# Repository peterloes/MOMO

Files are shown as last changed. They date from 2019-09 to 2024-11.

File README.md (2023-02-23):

# Multifunctional mainboard to observe and manipulate organisms (MOMO)
[\[paper\]](https://besjournals.onlinelibrary.wiley.com/doi/full/10.1111/1365-2656.13160) 2.3 Nest and feeder monitoring system

Authors: Loës P., Skripsky P., Kempenaers B. (2019) 

Platform for animal observation and manipulation. 

An efficient system to monitor and control animal behaviour in wildlife
as well as in laboratory settings.

- Targeted manipulation of 1000 and more individuals. Selective feeder.
- Supports a broad range of technical applications like e.g. traps, gates, feeders, lights, cameras
-	Compatible with different RFID systems and triggers
-	Low power consumption and specific data collection lead to long lasting collection periods
-	Applicable world-wide due to its compatibility with different types of radio clock receivers 
-	High observation quality through low disturbance to the animals
- Supports data-transfer to external devices, such as personal computers

My image

- Time Synchronization with atomic clock once a day to ensure optimal data quality
- Application Current Control twice a day
- Forecast for Battery-Change implemented
- Energy Bypass so that Date and Time are maintained even when changing battery
- Hyperterminal Output to get real-time data to the computer/laptop
- Low-Power Device:sleep: 220µA@12V with Light_Barrier awake: 12mA@12V

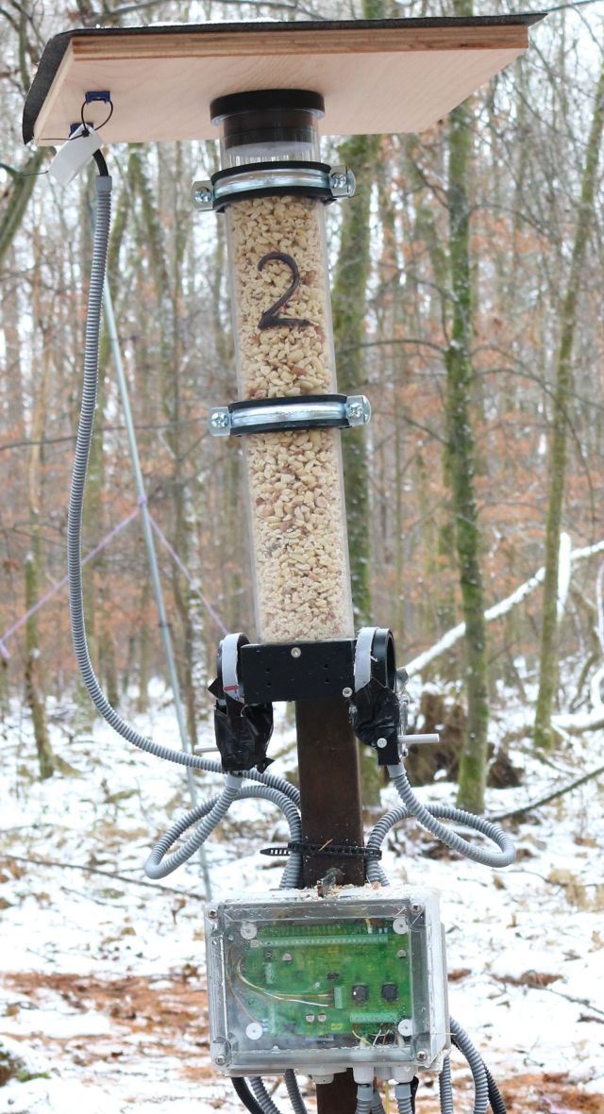
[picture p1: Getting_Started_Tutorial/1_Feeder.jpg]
My image


Bird Feeder Application:

https://github.com/peterloes/MOMO/blob/master/Getting_Started_Tutorial/1_poster_overview_3.pdf

Raw data on SD Card:

https://github.com/peterloes/MOMO/blob/master/Getting_Started_Tutorial/6_rawdata_BOX1005.TXT

Configuration data on SD Card:

https://github.com/peterloes/MOMO/blob/master/Software/CONFIG.TXT

Optional components: 

https://github.com/peterloes/Light_Barrier

https://github.com/peterloes/Servo_Engine

https://github.com/peterloes/Linear_Engine

https://github.com/peterloes/Booter_RFID-MS_MOMO_TAMDL

https://github.com/peterloes/Clock_receiver_RFID-MS_MOMO_TAMDL

Manufacture:

https://github.com/peterloes/MOMO/blob/master/Getting_Started_Tutorial/5_Supplier.txt

EXTENSIONS

Application Scales: Outdoor weighing system for animals include RFID-reader

https://github.com/peterloes/Scales

Application Audio: Record and playback soundfiles triggered by (RFID) pit-tag numbers

https://github.com/peterloes/Audio

C is the Greenest Programming Language

To achieve its power and energy-efficiency features, EFM32 products utilize ultralow active and idle power,
fast wakeup and processing times, and most important, the ability to intelligently interact with peripherals
and sensors autonomously without waking up the CPU and consuming more power.

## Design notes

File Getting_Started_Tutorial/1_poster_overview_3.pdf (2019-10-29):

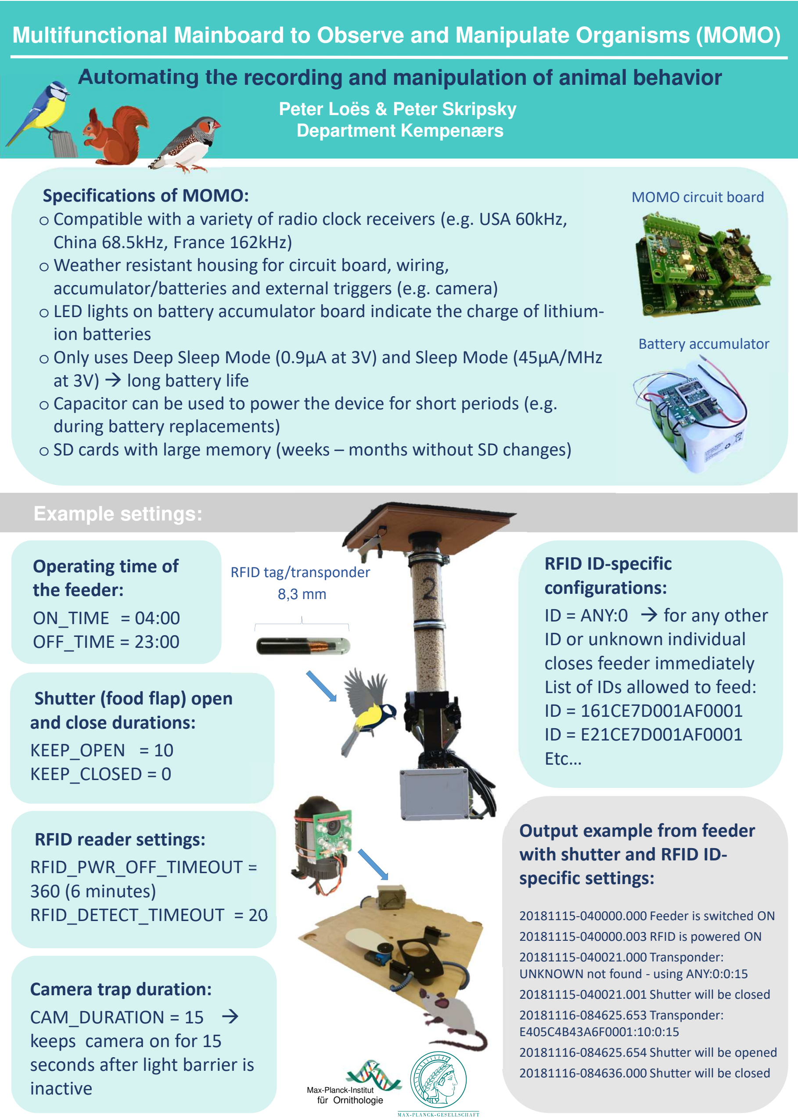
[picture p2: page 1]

### Multifunctional Mainboard to Observe and Manipulate Organisms (MOMO)

### Automating the recording and manipulation of animal behavior

Peter Loës & Peter Skripsky Department Kempenærs

Operating time of
the feeder:
ON_TIME = 04:00
OFF_TIME = 23:00

8,3 mm

RFID tag/transponder

RFID reader settings:
RFID_PWR_OFF_TIMEOUT =
360 (6 minutes)
RFID_DETECT_TIMEOUT = 20

Shutter (food flap) open
and close durations:
KEEP_OPEN = 10
KEEP_CLOSED = 0

Camera trap duration:
CAM_DURATION = 15 →
keeps camera on for 15
seconds after light barrier is inactive

RFID ID-specific
configurations:
ID = ANY:0 → for any other ID or unknown individual
closes feeder immediately
List of IDs allowed to feed: ID = 161CE7D001AF0001
ID = E21CE7D001AF0001
Etc…
Specifications of MOMO: | MOMO circuit board
- Compatible with a variety of radio clock receivers (e.g. USA 60kHz,
China 68.5kHz, France 162kHz)
- Weather resistant housing for circuit board, wiring,
accumulator/batteries and external triggers (e.g. camera)
- LED lights on battery accumulator board indicate the charge of lithiumion batteries
- Only uses Deep Sleep Mode (0.9μA at 3V) and Sleep Mode (45μA/MHz at 3V) → long battery life
- Capacitor can be used to power the device for short periods (e.g. during battery replacements)
- SD cards with large memory (weeks – months without SD changes)

Max-Planck-Institut
für Ornithologie

Example settings:

Battery accumulator

Output example from feeder with shutter and RFID ID-specific settings:

20181115-040000.000 Feeder is switched ON 20181115-040000.003 RFID is powered ON 20181115-040021.000 Transponder: UNKNOWN not found - using ANY:0:0:15 20181115-040021.001 Shutter will be closed 20181116-084625.653 Transponder: E405C4B43A6F0001:10:0:15
20181116-084625.654 Shutter will be opened 20181116-084636.000 Shutter will be closed

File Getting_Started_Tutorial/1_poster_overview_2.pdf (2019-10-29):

### Multifunctional Mainboard to Observe and Manipulate Organisms (MOMO)

### Automating the recording and manipulation of animal behavior

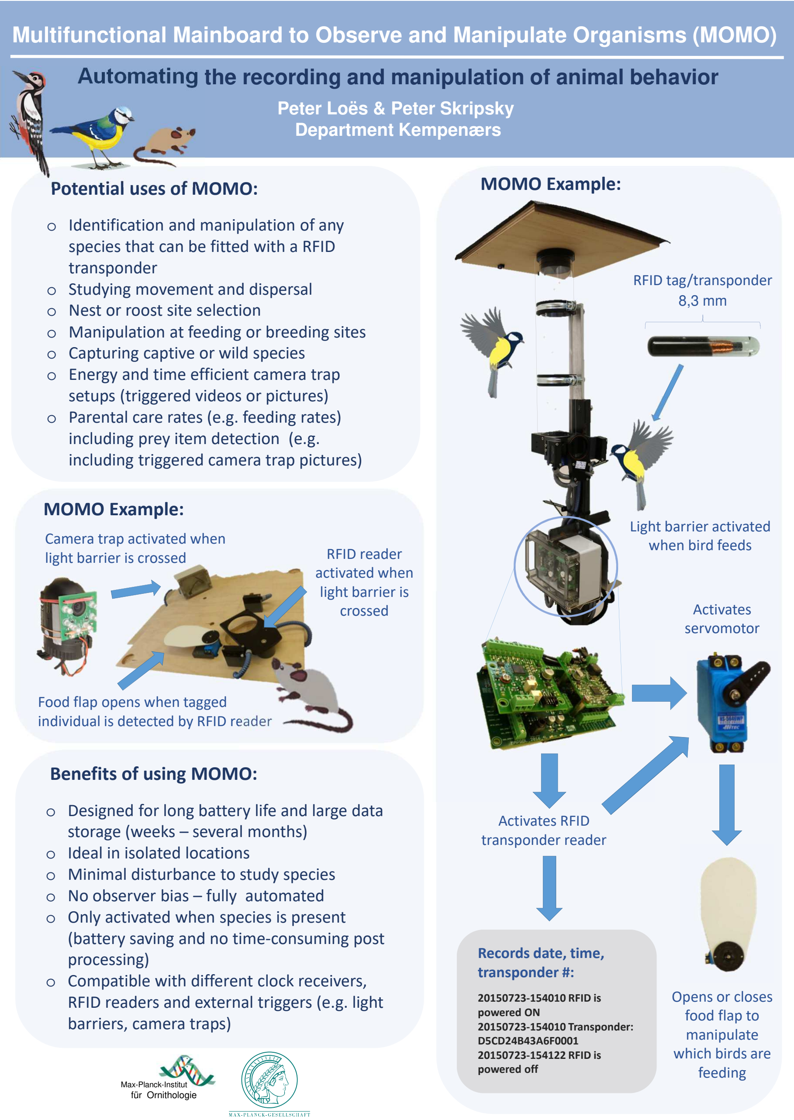
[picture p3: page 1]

Peter Loës & Peter Skripsky Department Kempenærs

Max-Planck-Institut
für Ornithologie

8,3 mm

RFID tag/transponder

Activates
servomotor

Opens or closes
food flap to
manipulate
which birds are
feeding

Light barrier activated
when bird feeds

Activates RFID
transponder reader

Records date, time,
transponder #:

20150723-154010 RFID is
powered ON
20150723-154010 Transponder: D5CD24B43A6F0001
20150723-154122 RFID is
powered off
Potential uses of MOMO: | MOMO Example:
- Identification and manipulation of any
species that can be fitted with a RFID
transponder
- Studying movement and dispersal
- Nest or roost site selection
- Manipulation at feeding or breeding sites
- Capturing captive or wild species
- Energy and time efficient camera trap setups (triggered videos or pictures)
- Parental care rates (e.g. feeding rates) including prey item detection (e.g. including triggered camera trap pictures)

Food flap opens when tagged individual is detected by RFID reader

RFID reader
activated when
light barrier is
crossed

Camera trap activated when light barrier is crossed

Benefits of using MOMO:

- Designed for long battery life and large data storage (weeks – several months)
- Ideal in isolated locations
- Minimal disturbance to study species
- No observer bias – fully automated
- Only activated when species is present (battery saving and no time-consuming post processing)
- Compatible with different clock receivers, RFID readers and external triggers (e.g. light barriers, camera traps)

MOMO Example:

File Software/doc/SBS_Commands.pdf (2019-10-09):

# Projekt U-BMS2-4

# SBS-

# Commands

# SBS Commands

Device Address | | | | | | 0x0A
ManufacturerAccess | | | | | | 0x00

Read word

RemainingCapacityAlarm | 0x01

Read word
Rückgabe des remainingCapacityAlarm-Wertes in [mAh].

Wenn die Restkapazität(remainingCapacity) kleiner als der Wert vom RemainingCapacityAlarm ist, sendet die Batterie eine Alarmwarnung zum Host. Der RemainingCapacityAlarm-Flag im Battery-Status wird gesetzt.

RemainingTimeAlarm | 0x02

Read word
Rückgabe des remainingTimeAlarm -Wertes in [min].

Wenn die durchschnittliche Entladezeit des Akkus(AverageTimeToEmpty) kleiner als der Wert vom
RemainingTimeAlarm | ist, | sendet | die | Batterie | eine | Alarmwarnung | zum | Host. | Der
RemainingTimeAlarm-Flag im Battery-Status wird gesetzt.
Battery Mode | | | | | | 0x03

Read word

Bit | Beschreibung

### 12 BALANCING CELL3

### 11 BALANCING CELL2

### 10 BALANCING CELL1

### 6 BALANCING CELL4

### 5 Deep Under Voltage recovery(DUVRD) Bit vom FET Control and Status-Register

(FCSR)

### 4 Current Protection Status (CPS) Bit vom FET Control and Status-Register (FCSR)

### 3 Discharge FET (DFE) Bit vom FET Control and Status-Register (FCSR)

### 2 Charge FET (CFE) Bit vom FET Control and Status-Register (FCSR)

CoreTemperature | 0x08

Read word
Die aktuelle Chip-Temperatur in [°K]
Voltage | 0x09

Read word
Die gesamte Akkuspannung in [mV]
BatteryCurrent | 0x0A

Read word
Der aktuelle Strom in [mA], der aus bzw. in den Akkupack durchfließt.
BatteryAverageCurrent | 0x0B

Read word
Der durchschnittliche Strom des Akkupacks in [mA]
RelativeStateOfCharge | 0x0D

Read word
Der relative Ladezustand des Akkupacks in [%]
AbsoluteStateOfCharge | 0x0E

Read word
Der absolute Ladezustand des Akkupacks in [%]
RemainingCapacity | 0x0F

Read word
Die Restkapazität des Akkupacks in [mAh]
FullChargeCapacity | 0x10

Read word
Rückgabe der vollen Ladekapazität in [mAh]
RunTimeToEmpty | 0x11

Read word
Die Ladezeit in [min]
AverageTimeToEmpty | 0x12

Read word
Die durchschnittliche Entladezeit [min]
AverageTimeToFull | 0x13

Read word
Die durchschnittliche Ladezeit in [min]

ChargingCurrent | 0x14

Read word
Der Ladestrom in [mA]
ChargingVoltage | 0x15

Read word
Die maximale Ladespannung in [mV]
Battery Status (flags) | 0x16

Read word

Bit | Beschreibung

### 15 Over Charged Alarm

Überprüfung des chargingProhibited-Flags

### 14 Terminate Charge Alarm

Überprüfung des voltageTooHigh-Flags

### 12 Over Temp Alarm

Überprüfung des cellTemperatureTooHigh -Flags

### 11 Terminante Discharge Alarm

Dieses Bit wird gesetzt, wenn die Restkapazität unter dem definierten Wert von SBS_TERMINATE_DISCHARGE_LIMIT (Standard 5mAh) liegt. Wenn ein Ladegerät erkannt wird, wird dieses Bit gelöscht.

### 10 Battery Protection Triggered

Dieses Bit wird gesetzt, wenn die Batterieschutz-Hardware die FETs ausschaltet.

### 9 Remaining Capacity Alarm

Dieses Bit wird gesetzt, wenn die Restkapazität weniger als der definierte Wert des Restkapazität-Alarms(RemainingCapacityAlarm) ist.

### 8 Remaining Time Alarm :

Wenn die durchschnittlische Entladezeit (AverageTimeToEmpty) kleiner als der definierte Wert des Entladezeit-Alarms (RemainingTimeAlarm) ist, wird dieses Bit gesetzt.

### 7 Initialized

Dieses Bit wird gesetzt, wenn die Initialisierung erfolgreich abgeschlossen ist.

### 6 Discharging

Dieses Bit wird gesetzt, wenn ein Entladestrom fließt.

### 5 Fully Charged

Dieses Bit wird gesetzt, wenn die Batterie vollständig geladen ist. Wenn ein Entladestrom aus der Batterie fließt, der höher als der Standby-Stromwert ist, wird dieses Bit gelöscht.

### 4 Fully Discharged

Dieses Bit wird gesetzt, wenn die Restkapazität der Batterie bzw. die Zellenspannung sehr niedrig ist. Wenn der relative Ladezustand über 20% steigt, wird dieses Bit gelöscht.

ChargerCycleCount | 0x17

Read word
Die Anzahl der Ladezyklen
DesignCapacity | 0x18

Read word
Die Nennkapazität in [mAh]
DesignVoltage | 0x19

Read word
Die Nennspannung in [mV]
SpecificationInfo | 0x1A

Read word
Die Spezifikation-Info (Version und Revision-Nummer)
ManufactureDate | 0x1B

Read word
Das Herstellungsdatum
SerialNumber | 0x1C

Read word
Die Seriennummer
ManufacturerName | 0x20

Read Block
Der Name des Herstellers
DeviceName | 0x21

Read Block
Der Name des Gerätes
DeviceChemistry | 0x22

Read Block
Die chemische Bezeichnung des Gerätes
ManufacturerData | 0x23

Read Block
Die Herstellerdaten
ShuntResistance | 0x2A

Read word
Der Wert des Shunt-Widerstands in [µOhm]

CellsInSeries | 0x3C

Read word
Anzahl der verwendeten Zellen in Serie
OverCurrentReactionTime | 0x3D

Read word
Überstrom Reaktionszeit Stufe 1
OverCurrentCharge | 0x3E

Read word
Überladestrom Stufe 1
OverCurrentDischarge | 0x3F

Read word
Überentladestrom Stufe 1
HighCurrentReactionTime | 0x40

Read word
Überstrom Reaktionszeit Stufe 2
HighCurrentCharge | 0x41

Read word
Überladestrom Reaktionszeit Stufe 2
HighCurrentDischarge | 0x42

Read word
Überentladestrom Stufe 2
VoltageCell4 | 0x44

Read word
Rückgabe der Spannung der Zelle 4 in [mV]
VoltageCell3 | 0x45

Read word
Rückgabe der Spannung der Zelle 3 in [mV]
VoltageCell2 | 0x46

Read word
Rückgabe der Spannung der Zelle 3 in [mV]

VoltageCell1 | 0x47

Read word
Rückgabe der Spannung der Zelle 1 in [mV]
CellMinVoltage | 0x54

Read word
Die minimale Zellenspannung in [mV]
CellMaxVoltage | 0x55

Read word
Der Wert der maximalen Zellenspannung in [mV]
CellPowerOffVoltage | 0x55

Read word
Der Wert der Zellenspannung in [mV], bei der das BMS in den PowerOffModus geht

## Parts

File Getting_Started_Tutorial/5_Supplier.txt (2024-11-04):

Active antennas
DCF77 Empfänger AASV DCFn PON/Ri/1m Aktivantenne SV DCFn 

HKW-Elektronik GmbH
Jörg Schneider

Eisenacher Str. 42 b
99848 Wutha-Farnroda / Thür.
Germany
Phone:  +49 (0)36921 3080 130
mailto:    schneider@hkw-elektronik.de
www.hkw-elektronik.de

Lightbarriers for front plate
Doppel - Lichtschranke Art.Nr. P00700 (Lichtschranken in Frontplatten):

SWISSSENSOR AG
Geschäftsleitung Hermann Beer

Steinacherstrasse 4
CH-9327 Tübach
Germany
Tel. +41(0)71 845 24 24
mailto:beer@swisssensor.ch
www.swisssensor.ch

Lithium Ionen rechargeable battery pack Art.Nr. 60.16294 Panasonic NCR 18650GA 4S2P
14,4Volt 6900mAh inklusive SMBus Kabel je. 150mm 

DYNAMIS Batterien GmbH
Josef Pfeil

Brühlstraße 15  D- 78465 Dettingen / Konstanz
Tel. +49 (0) 75 33/93 669-15
mailto:josef.pfeil@dynamis-batterien.de
www.dynamis-batterien.de

RFID reader
Nanomodule Multi 125LV A/1.11 (T3NM-LV) 125kHz +/-0,5% Art.Nr. ART10413
ANT002 Rundspule 47mm, 490µH Art.Nr. ART 10668

Elatec GmbH
Felix Ellspermann

Zeppelinstr. 1
82178 Puchheim 
Germany
Tel: +49 89 552 9961 120
mailto: f.ellspermann@elatec.com
www.elatec-rfid.com

Small sized transponder, not uniqued.
GlassTag 1,41x8,3mm EM4305 134kHz

Programming required for transponders.

Rasmus Forntheil
Product Manager Animal ID
RBIS Europe, Smartrac Specialty GmbH

e: rasmus.forntheil@eu.averydennison.com
t: +49 (0) 2265 9919-14  |  m: +49 (0) 173 5688184
Gewerbeparkstr. 10, 51580 Reichshof-Wehnrath, Germany

Internet: https://www.averydennison.com/en/home.html

Supplier of all Electronic Boards

Top-Print Electronic GmbH
Oskar Schmid

Rosenheimer Landstr. 129a
85521 Ottobrunn
Germany
Tel.: +49-89-60668047
Fax: +49-89-60668049
mailto: info@top-print.eu
https://www.leiterplatten-muenchen.de/

Protective coating with Schmelzharz Bectron MR3404

KC – Kunststoff- Chemische Produkte GmbH
Holger Sarau-Burghardt

Leonberger Straße 86 
DE 71292 Friolzheim
phone: +49 (0)7044 9425 13
e-mail: h.sarau-burghardt@kc-produkte.com
http: www.conformalcoating.de

Industrial SD Cards ATP 2GB
https://www.atpinc.com/products/industrial-sd-cards

FTDI Chip cable (3.5mm Audio Jack to USB)
TTL-232R-3V3-AJ

Housing
https://www.spelsberg.de/industrieleergehaeuse/glatt-mit-befestigungsnocken/20100701/
TG PC 1612-9-to
Artikelnummer: 20100701 | Maße: 162 x 122 x 90 mm
Leergehäuse IP66 / IP67 Polycarbonat

Docklight RS232 Terminal / RS232 Monitor
https://docklight.de/information/

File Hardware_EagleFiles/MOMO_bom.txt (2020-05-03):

Partlist exported at 5/22/2017 10:02:44 AM

Part  Value                 Device                  Package                Description                                                    MF MPN     OC_FARNELL OC_NEWARK PACKAGE  SUPPLIER         
C1    100µF/25V             CPOL-EUE                PANASONIC_E            POLARIZED CAPACITOR, European symbol                                                                                     
C2    10µF/25V              C-EUC1206               C1206                  CAPACITOR, European symbol                                                                                               
C3    22µF/10V              C-EUC0603               C0603                  CAPACITOR, European symbol                                                                                               
C4    EECS0HD 224;Panasonic GOLDCAPSPK-V            GOLDCAPSPK-V                                                                                                                                    
C5    100µF/25V             CPOL-EUE                PANASONIC_E            POLARIZED CAPACITOR, European symbol                                                                                     
C6    100µF/25V             CPOL-EUE                PANASONIC_E            POLARIZED CAPACITOR, European symbol                                                                                     
C7    100µF/25V             CPOL-EUE                PANASONIC_E            POLARIZED CAPACITOR, European symbol                                                                                     
C8    100nF/16V             C-EUC0805               C0805                  CAPACITOR, European symbol                                                                                               
C9    100nF/16V             C-EUC0805               C0805                  CAPACITOR, European symbol                                                                                               
C10   100nF/16V             C-EUC0805               C0805                  CAPACITOR, European symbol                                                                                               
C11   10µ/25V               C-EUC1206               C1206                  CAPACITOR, European symbol                                                                                               
C12   100n                  C_SMD0805               0805                                                                                                                                            
C13   1u                    C_SMD0805               0805                                                                                                                                            
C14   12p                   C_SMD0805               0805                                                                                                                                            
C15   18p                   C_SMD0805               0805                                                                                                                                            
C16   100n                  C_SMD0805               0805                                                                                                                                            
C17   100n                  C_SMD0805               0805                                                                                                                                            
C18   100n                  C_SMD0805               0805                                                                                                                                            
C19   12p                   C_SMD0805               0805                                                                                                                                            
C20   18p                   C_SMD0805               0805                                                                                                                                            
C21   10µ                   C_SMD0805               0805                                                                                                                                            
C22   100n                  C_SMD0805               0805                                                                                                                                            
C23   100n                  C_SMD0805               0805                                                                                                                                            
C24   100n                  C_SMD0805               0805                                                                                                                                            
C25   100n                  C_SMD0805               0805                                                                                                                                            
C26   100n                  C_SMD0805               0805                                                                                                                                            
C27   10µ                   C_SMD0805               0805                                                                                                                                            
C28   100nF                 C-EUC0603               C0603                  CAPACITOR, European symbol                                                                                               
C29   100nF                 C-EUC0603               C0603                  CAPACITOR, European symbol                                                                                               
C30   100nF                 C-EUC0603               C0603                  CAPACITOR, European symbol                                                                                               
C31   100nF                 C-EUC0603               C0603                  CAPACITOR, European symbol                                                                                               
C32   100nF                 C-EUC0603               C0603                  CAPACITOR, European symbol                                                                                               
C33   4.7µF                 C-EUC1210               C1210                  CAPACITOR, European symbol                                                                                               
C34   4.7µF                 C-EUC1210               C1210                  CAPACITOR, European symbol                                                                                               
C35   n.b.                  C-EUC1210               C1210                  CAPACITOR, European symbol                                                                                               
C36   n.b.                  C-EUC1210               C1210                  CAPACITOR, European symbol                                                                                               
C37   10nF                  C-EUC0603               C0603                  CAPACITOR, European symbol                                                                                               
C38   10nF                  C-EUC0603               C0603                  CAPACITOR, European symbol                                                                                               
C39   100nF                 C-EUC0603               C0603                  CAPACITOR, European symbol                                                                                               
C40   100nF                 C-EUC0603               C0603                  CAPACITOR, European symbol                                                                                               
C41    n.b.                 C-EUC0603               C0603                  CAPACITOR, European symbol                                                                                               
C42    n.b.                 C-EUC0603               C0603                  CAPACITOR, European symbol                                                                                               
C43   4.3nF                 C-EUC0603               C0603                  CAPACITOR, European symbol                                                                                               
C44   4.3nF                 C-EUC0603               C0603                  CAPACITOR, European symbol                                                                                               
C45   24pF                  C-EUC0603               C0603                  CAPACITOR, European symbol                                                                                               
C46   24pF                  C-EUC0603               C0603                  CAPACITOR, European symbol                                                                                               
C47    n.b.                 C-EUC0603               C0603                  CAPACITOR, European symbol                                                                                               
C48    n.b                  C-EUC0603               C0603                  CAPACITOR, European symbol                                                                                               
C49   22µF                  C-EUC1210               C1210                  CAPACITOR, European symbol                                                                                               
C50   22µF                  C-EUC1210               C1210                  CAPACITOR, European symbol                                                                                               
C51   22µF                  C-EUC1210               C1210                  CAPACITOR, European symbol                                                                                               
C52   22µF                  C-EUC1210               C1210                  CAPACITOR, European symbol                                                                                               
C53   n.b.                  C-EUC1210               C1210                  CAPACITOR, European symbol                                                                                               
C54   n.b.                  C-EUC1210               C1210                  CAPACITOR, European symbol                                                                                               
C55   100nF                 C-EUC0603               C0603                  CAPACITOR, European symbol                                                                                               
C56   100nF                 C-EUC0603               C0603                  CAPACITOR, European symbol                                                                                               
C57   10n                   C-EUC0603               C0603                  CAPACITOR, European symbol                                                                                               
D1    BAT54C                D2A_SOT23               SOT-23$1               Dual DIODE                                                                                                               
D2    BAT54C                D2A_SOT23               SOT-23$1               Dual DIODE                                                                                                               
D3    BAT54C                D2A_SOT23               SOT-23$1               Dual DIODE                                                                                                               
D4    BAT54C                D2A_SOT23               SOT-23$1               Dual DIODE                                                                                                               
D5    B360B                 SCHOTTKY-DIODESMD       SMB                    Schottky Diode                                                                                                           
D6    B360B                 SCHOTTKY-DIODESMD       SMB                    Schottky Diode                                                                                                           
F1    MF-USMF110            PFUF                    PFUF_1210POLY                                                                                                                                   
F2    MF-USMF110            PFUF                    PFUF_1210POLY                                                                                                                                   
F3    MF-USMF150            PFUF                    PFUF_1210POLY                                                                                                                                   
F4    MF-USMF150            PFUF                    PFUF_1210POLY                                                                                                                                   
F5    MF-USMF110            PFUF                    PFUF_1210POLY                                                                                                                                   
F6    MF-USMF110            PFUF                    PFUF_1210POLY                                                                                                                                   
IC1   TPS62125              TPS62125                DSG_PWSO-N8_EXP                                                                                                                                 
IC2   EFM32G230F128         EFM32G230F128           QFN64                  EFM32G230F128 Gecko Microcontroller in 9mm x 9mm QFN64 package                                                           
IC3   TPS54240DGQR          TPS54240DGQR            S-PDSO-G10                                                                                                                                      
IC4   TPS54240DGQR          TPS54240DGQR            S-PDSO-G10                                                                                                                                      
J1    LUMBERG1502_01        LUMBERG1502_01          LUMBERG1502_01                                                                                                                                  
L1    LPS3008/22µH          LPS3008                 LPS3008                                                                                                                                         
L2    BLM21B102S            WE-CBF-7427920_0805     0805                   SMD EMI Suppression Ferrite Beads WE-CBF                          7427920 1635707    08P2358   IND-0805 Wuerth Elektronik
L3    PIS4728-220M-04       DR127                   DR127                  High Power Density, High Efficiency, Shielded Inductors                                                                  
L4    PIS4728-220M-04       DR127                   DR127                  High Power Density, High Efficiency, Shielded Inductors                                                                  
LED1  SML-H12U8TT86         LEDCHIPLED_0805         CHIPLED_0805           LED                                                                                                                      
LED2  SML-H12Y8TT86         LEDCHIPLED_0805         CHIPLED_0805           LED                                                                                                                      
LED3  (n.b.)                LEDCHIPLED_0805         CHIPLED_0805           LED                                                                                                                      
LED4  (n.b.)                LEDCHIPLED_0805         CHIPLED_0805           LED                                                                                                                      
LSP1  (n.b.)SE13            SE13                    SE13                   SOLDER PAD E1542,  drill 1,3mm, distributor Buerklin, 07F815                                                             
LSP2  (n.b.)SE13            SE13                    SE13                   SOLDER PAD E1542,  drill 1,3mm, distributor Buerklin, 07F815                                                             
PASS1 ROUND_1MM1.5          ROUND_1MM1.5            ROUND2_1.5MM                                                                                                                                    
PASS2 ROUND_1MM1.5          ROUND_1MM1.5            ROUND2_1.5MM                                                                                                                                    
Q1    SI7121DN              TRANSISTOR-FET_SI7113DN TRANSISTOR-FET_1212-8S                                                                                                                          
Q2    NX5032GA/32MHz/8pF    CRYSTAL2P5.0X3.2        CRYSTAL2P5.0X3.2       Quarz Crystal                                                                                                            
Q3    CM7V, 32768Hz/12.5pF  CRYSTAL2P               CRYSTAL2P3.2X1.5       Quarz Crystal                                                                                                            
R1    100k                  R-EU_R0805              R0805                  RESISTOR, European symbol                                                                                                
R2    1K2                   R-EU_R0805              R0805                  RESISTOR, European symbol                                                                                                
R3    1M47                  R-EU_R0805              R0805                  RESISTOR, European symbol                                                                                                
R4    200K                  R-EU_R0805              R0805                  RESISTOR, European symbol                                                                                                
R5    30K9                  R-EU_R0805              R0805                  RESISTOR, European symbol                                                                                                
R6    1K2                   R-EU_R0805              R0805                  RESISTOR, European symbol                                                                                                
R7    100K                  R-EU_R0805              R0805                  RESISTOR, European symbol                                                                                                
R8    2M                    R-EU_R0805              R0805                  RESISTOR, European symbol                                                                                                
R9    560K                  R-EU_R0805              R0805                  RESISTOR, European symbol                                                                                                
R10   100                   R-EU_R0805              R0805                  RESISTOR, European symbol                                                                                                
R11   1                     R-EU_R0805              R0805                  RESISTOR, European symbol                                                                                                
R12   100                   R-EU_R0805              R0805                  RESISTOR, European symbol                                                                                                
R13   100K                  R-EU_R0805              R0805                  RESISTOR, European symbol                                                                                                
R14   100K                  R-EU_R0805              R0805                  RESISTOR, European symbol                                                                                                
R15   1K                    R-EU_R0805              R0805                  RESISTOR, European symbol                                                                                                
R16   100                   R-EU_R0805              R0805                  RESISTOR, European symbol                                                                                                
R17   1K                    R-EU_R0805              R0805                  RESISTOR, European symbol                                                                                                
R18   100K                  R-EU_R0805              R0805                  RESISTOR, European symbol                                                                                                
R19   10K                   R-EU_R0805              R0805                  RESISTOR, European symbol                                                                                                
R20   10K                   R-EU_R0805              R0805                  RESISTOR, European symbol                                                                                                
R21   1K                    R-EU_R0805              R0805                  RESISTOR, European symbol                                                                                                
R22   1K                    R-EU_R0805              R0805                  RESISTOR, European symbol                                                                                                
R23   (n.b.)10K             R-EU_R0805              R0805                  RESISTOR, European symbol                                                                                                
R24   10K                   R-EU_R0805              R0805                  RESISTOR, European symbol                                                                                                
R25   10K                   R-EU_R0805              R0805                  RESISTOR, European symbol                                                                                                
R26   100                   R-EU_R0805              R0805                  RESISTOR, European symbol                                                                                                
R27   100                   R-EU_R0805              R0805                  RESISTOR, European symbol                                                                                                
R28   100K                  R-EU_R0805              R0805                  RESISTOR, European symbol                                                                                                
R29   100K                  R-EU_R0805              R0805                  RESISTOR, European symbol                                                                                                
R30   100K                  R-EU_R0805              R0805                  RESISTOR, European symbol                                                                                                
R31   100                   R-EU_R0805              R0805                  RESISTOR, European symbol                                                                                                
R32   100K                  R-EU_R0805              R0805                  RESISTOR, European symbol                                                                                                
R33   100                   R-EU_R0805              R0805                  RESISTOR, European symbol                                                                                                
R34   100K                  R-EU_R0805              R0805                  RESISTOR, European symbol                                                                                                
R35   100K                  R-EU_R0805              R0805                  RESISTOR, European symbol                                                                                                
R36   100                   R-EU_R0805              R0805                  RESISTOR, European symbol                                                                                                
R37   100K                  R-EU_R0805              R0805                  RESISTOR, European symbol                                                                                                
R38   100                   R-EU_R0805              R0805                  RESISTOR, European symbol                                                                                                
R39   100K                  R-EU_R0805              R0805                  RESISTOR, European symbol                                                                                                
R40   100K                  R-EU_R0805              R0805                  RESISTOR, European symbol                                                                                                
R41   100                   R-EU_R0805              R0805                  RESISTOR, European symbol                                                                                                
R42   100K                  R-EU_R0805              R0805                  RESISTOR, European symbol                                                                                                
R43   100K                  R-EU_R0805              R0805                  RESISTOR, European symbol                                                                                                
R44   100K                  R-EU_R0805              R0805                  RESISTOR, European symbol                                                                                                
R45   348K                  R-EU_R0805              R0805                  RESISTOR, European symbol                                                                                                
R46   348K                  R-EU_R0805              R0805                  RESISTOR, European symbol                                                                                                
R47   0                     R-EU_R0805              R0805                  RESISTOR, European symbol                                                                                                
R48   0                     R-EU_R0805              R0805                  RESISTOR, European symbol                                                                                                
R49   39K                   R-EU_R0805              R0805                  RESISTOR, European symbol                                                                                                
R50   39K                   R-EU_R0805              R0805                  RESISTOR, European symbol                                                                                                
R51   0                     R-EU_R0805              R0805                  RESISTOR, European symbol                                                                                                
R52   0                     R-EU_R0805              R0805                  RESISTOR, European symbol                                                                                                
R53   0                     R-EU_R0805              R0805                  RESISTOR, European symbol                                                                                                
R54   53K                   R-EU_R0805              R0805                  RESISTOR, European symbol                                                                                                
R55   10k                   R-EU_R0805              R0805                  RESISTOR, European symbol                                                                                                
R56   0                     R-EU_R0805              R0805                  RESISTOR, European symbol                                                                                                
R57   53K                   R-EU_R0805              R0805                  RESISTOR, European symbol                                                                                                
R58   10K                   R-EU_R0805              R0805                  RESISTOR, European symbol                                                                                                
R59   (n.b.)                R-EU_R0805              R0805                  RESISTOR, European symbol                                                                                                
R60   (n.b.)                R-EU_R0805              R0805                  RESISTOR, European symbol                                                                                                
R61   100                   R-EU_R0805              R0805                  RESISTOR, European symbol                                                                                                
R62   100                   R-EU_R0805              R0805                  RESISTOR, European symbol
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

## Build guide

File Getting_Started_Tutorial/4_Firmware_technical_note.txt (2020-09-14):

MOMO (Multifunctional Mainboard to Observe and Manipulate Organisms) 
is an application to automate the recording and manipulation of animal behavior.

Version 1.4
- Added support for battery controller TI bq40z50.
  LogBatteryInfo: Removed SBS_ManufacturerData.
  Display SBS_RunTimeToEmpty in days/hours/min.
  Display SBS_SerialNumber as hex value.
- CheckAlarmTimes to call the respective alarm action if the current time matches the alarm time.
  Reading the configuration file CONFIG.TXT from the SD-Card and set-up alarm action.
- Corrected decoding of Short-Range(SR) RFID Reader transponder ID.

This application consists of the following modules:
 - main.c - Initialization code and main execution loop.
 - DMA_ControlBlock.c - Control structures for the DMA channels.
 - Control.c - Sequence Control module.
 - CfgData.c - Handling of configuration data.
 - ExtInt.c - External interrupt handler.
 - AlarmClock.c - Alarm clock and timers facility.
 - DCF77.c - DCF77 Atomic Clock Decoder
 - clock.c - An implementation of the POSIX time() function.
 - LightBarrier.c - Interrupt logic for the two light barriers,
   enables the RFID reader.
 - RFID.c - RFID reader to receive transponder IDs.
 - BatteryMon.c - Battery monitor, periodically reads the state of the
   battery via the SMBus.
 - LEUART.c - The Low-Energy UART can be used as monitoring and debugging
   connection to a host computer.
 - microsd.c - Together with the files "diskio.c" and "ff.c", this module
   provides an implementation of a FAT file system on the @ref ss8.
 - Logging.c - Logging facility to send messages to the LEUART and store
   them into a file on the SD-Card.
 - PowerFail.c - Handler to switch off all loads in case of Power Fail.
 - The list of Transponder IDs is no more kept in memory, instead
   the configuration file is read for each compare.  This allows
   a higher number of IDs to be used (no memory limitations).

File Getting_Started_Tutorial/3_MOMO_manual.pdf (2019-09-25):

## Max Planck Institute for Ornithology

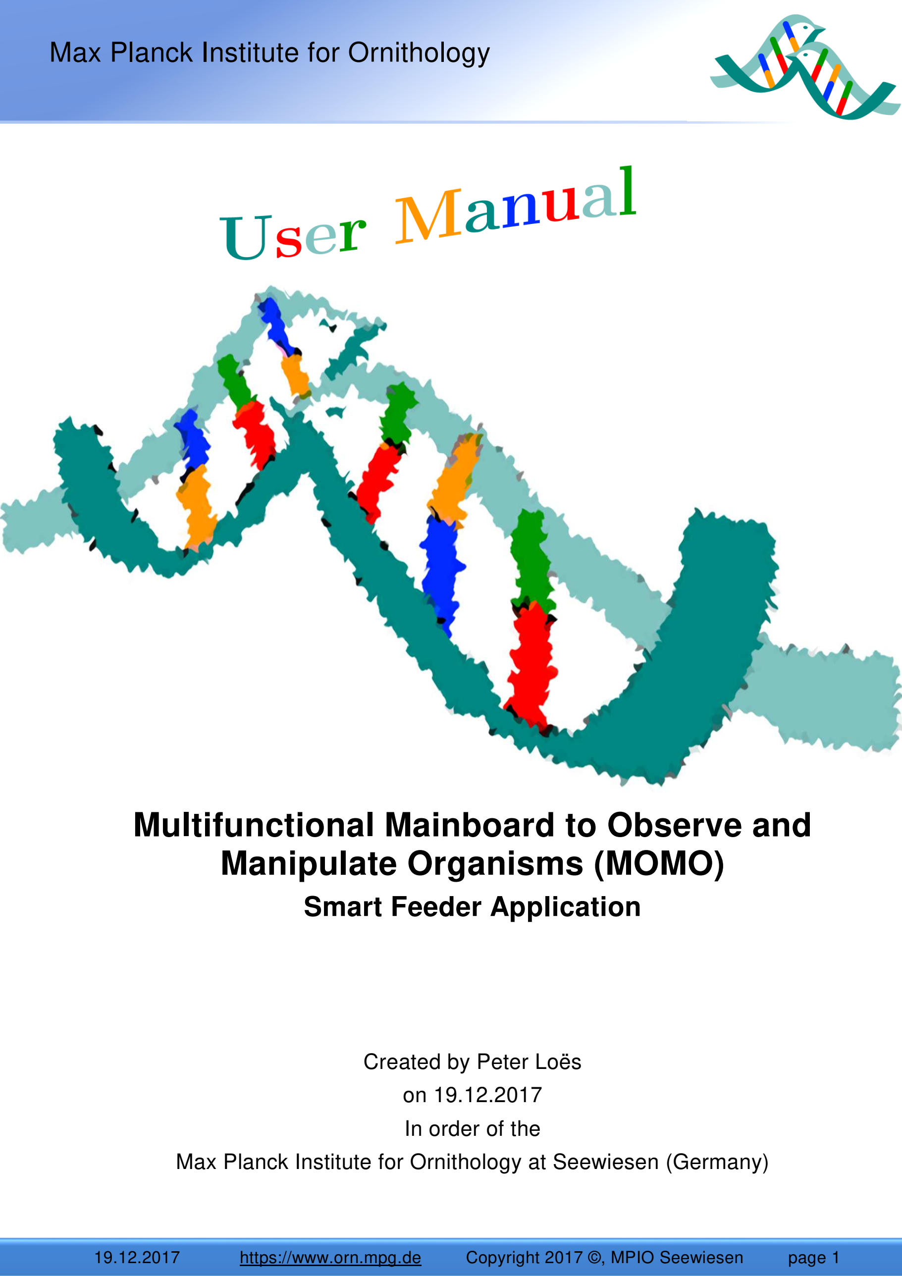
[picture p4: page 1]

19.12.2017 | https://www.orn.mpg.de | Copyright 2017 ©, MPIO Seewiesen | page 1

# Multifunctional Mainboard to Observe and Manipulate Organisms (MOMO)

## Smart Feeder Application

Created by Peter Loës
on 19.12.2017
In order of the
Max Planck Institute for Ornithology at Seewiesen (Germany)

Disclaimer and Copyright

19.12.2017 | https://www.orn.mpg.de | Copyright 2017 ©, MPIO Seewiesen | page 2

## Disclaimer

The Multifunctional Mainboard to Observe and Manipulate Organisms is to be used only as that described in this document. Any other method of usage is not permitted. If damage occurs due to incorrect usage, the manufacturer of the Multifunctional Mainboard to Observe and Manipulate Organisms is not liable.

## Copyright ©

The Copyright for this user manual remains with the manufacturer. Text and figures meet the latest technical status at the time of publication. Subject to change. The content of the user manual shall not affect any claims of the purchaser. The editor also welcomes suggestions of any possible improvements you may have or whether any errors are encountered.

List of abbrevations

19.12.2017 | https://www.orn.mpg.de | Copyright 2017 ©, MPIO Seewiesen | page 3

## List of abbreviations

SF | Smart Feeder
LB | Light Barrier
RFID | radio-frequency identification
EFM | Energy Friendly Microcontroller
PCB | printed circuit board
DCF | D for Deutschland (Germany), C for long-wave transmitter, F due to the vicinity to the Town Frankfurt
ARM | Advanced RISC Machines
SD-CARD | Secure Digital Memory Card
PIT | Passive Integrated Transponder
LEUART | Low Energy Universal Asynchronous Receiver/Transmitter
USB | Universal Serial Bus
MOMO | Multifunctional Mainboard to Observe and Manipulate Organisms

System Overview

19.12.2017 | https://www.orn.mpg.de | Copyright 2017 ©, MPIO Seewiesen | page 4

## System Overview

## General Description of Functions

The Multifunctional Mainboard to Observe and Manipulate Organisms has been developed to record and manipulate animal behaviour. For this purpose, animals got equipped with transponders that can be activated and identified via reading devices. Every animal equipped with a transponder can thereby be identified individually. This technology can be used for every animal species on or in which it is possible to attach a RFID transponder of the size of a rice grain.

Within a population of several individuals carrying a RFID transponder, the Multifunctional Mainboard to Observe and Manipulate Organisms can save the presence and identity of the animals. Whenever an individual with transponder visits a feeder equipped with sensors, the sensor data, transponder code and the timestamp are saved on a SD-card.

Video recordings and visual observations have long been used by biologists to document behaviour of animals and to answer questions about territory, distribution and reproductive behaviour. However, these methods are time consuming, often inexact, and cannot be used when visibility is low (e.g. at night).

To achieve a flexible operation in the field, the Multifunctional Mainboard to Observe and Manipulate Organisms is supplied with electrical energy by a rechargeable accumulator.

The use of electronic devices in the field and nature requires special features in order to operate correctly. Special developments are needed in order to cope with changes in ambient temperature, humidity, pressure and when the electrical power grid is unavailable. However, such developments can be time-consuming and cost-intensive.

Many iterations in the development are needed in order to ensure a stable functioning of electronic products in the wild.

System Overview

19.12.2017 | https://www.orn.mpg.de | Copyright 2017 ©, MPIO Seewiesen | page 5

The Multifunctional Mainboard to Observe and Manipulate Organisms should be placed where the animals of interest often visit, such as feeders, nests, roosts, enclosures or bottlenecks.

One main usage for which the Multifunctional Mainboard to Observe and Manipulate Organisms was developed, is the feeder. Bird behaviour can be manipulated by rationing or even blocking their access to food. The so called ‘Smart Feeder’ records the bird’s presence and therefore provides information about their distribution and foraging behaviour.

A key strength of the Multifunctional Mainboard to Observe and Manipulate Organisms is that it runs autonomously. During the development, special attention was paid developing an energy saving operation, so that a battery pack would only have to be changed every two weeks up to several months, depending on the activity of the smart feeder. The SD cards used have enough memory space to save data for several months of data collection. These low operating expenses make the Multifunctional Mainboard to Observe and Manipulate Organisms (MOMO) ideal for a use in isolated locations without grid connection. Furthermore, biological data is optimally collected when disturbance to the animal’s behaviour due to human presence is minimised. Compared with video recordings and observations, data generation is less error-prone and an increase of data volume is easily realizable. Nevertheless, MOMO also supports an activation and deactivation of video devices or cameras.

MOMO regularly surveys and documents the state of the smart feeder electronic system. A regular evaluation of these data can detect faulty systems and a necessary maintenance can be performed.

The Multifunctional Mainboard to Observe and Manipulate Organisms is currently used for animals with a diameter of less than 70mm, which is contingent upon the antenna of an animal transponder reader. Larger antennas with only marginal overhead are imaginable though, enabling a detection of larger animals as well.

System Overview

19.12.2017 | https://www.orn.mpg.de | Copyright 2017 ©, MPIO Seewiesen | page 6

Some examples of potential uses are:

- nest boxes of birds
- roosting boxes of bats
- studying and monitoring mammals like rats, mice, hamsters, badgers,

squirrels
- reptile research
- studying and monitoring fish
- studying breeding behaviour
- studying movement and dispersal of animals
- choice of nest boxes or roosts

System Overview

19.12.2017 | https://www.orn.mpg.de | Copyright 2017 ©, MPIO Seewiesen | page 7

## System configuration main circuit board

The smart feeder was developed over several years. After five years of development a reliable and efficient version was completed, which is described comprehensively in this manual. Additional detailed information, particularly concerning the electronic configuration, can be found in the datasheet.

Hardware Illustration (MOMO)

System Overview

19.12.2017 | https://www.orn.mpg.de | Copyright 2017 ©, MPIO Seewiesen | page 8
1 | Reset push button | 14 | Gold Cap Capacitor
2 Connections for linear actuator | control | 15 Connecting terminal for the radio clock
3 Connections for two passive | infrared detectors [3.5V@200mA] | 16 Output voltage | 3.5V-11V@ 2.5A for e.g. cameras
4 | Connections for limit switch | 17 | Output voltage 3.5V-11V@ 2.5A for e.g. cameras
5 Power supply for servomotor | [12V@1.5A] | 18 Power supply light barrier
6 Power supply for linear actuator | [12V@1.5A] | 19 Connecting terminal for switchable | RFID readers[12V@0.22A]
7 Connections for switchable power | supplies for three RFID readers | 20 | Connections for the SMBus „System Management Bus“ of the battery pack
8 | Power supply for MOMO | 21 | LEUART connector
9 | Down converter | 22 | LED display devices
10 Switchable power supply for three | RFID readers [3.5V@200mA] | 23 Connections for RFID reader serial bus
11 | Debug Interface | 24 | Connections for buses of the three RFID readers
12 Connections for buses of | servomotor | 25 Two connecting terminals for output of | 3.5V-11V@ 2.5A for e.g. cameras

13 Microcontroller EFM32G230

System Overview

19.12.2017 | https://www.orn.mpg.de | Copyright 2017 ©, MPIO Seewiesen | page 9

Buttons

A ‘reset’ pushbutton is installed on the mainboard of the Multifunctional Mainboard to Observe and Manipulate Organisms, which restarts MOMO.

Connections for linear actuator control

A linear drive or linear drive system refers to all drive systems that lead to a translational movement. Linear drives enable the movement of machines (or elements of them) and facilities (or parts of them) on a straight line or on other default routes.

System Overview

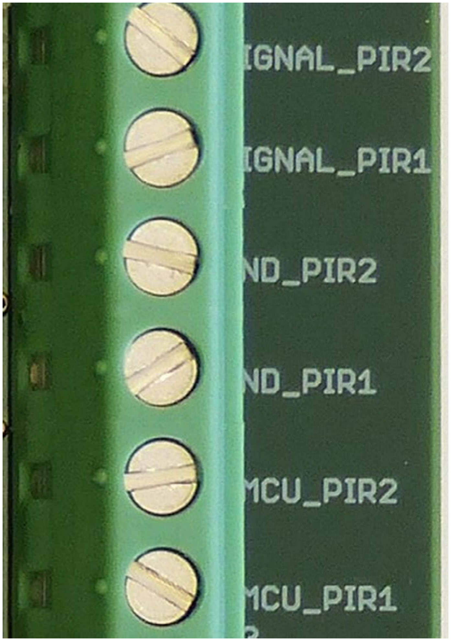
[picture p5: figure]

19.12.2017 | https://www.orn.mpg.de | Copyright 2017 ©, MPIO Seewiesen | page 10

Connections for two passive infrared detectors

A motion sensor is an electronic sensor, which detects movements within its proximity, enabling it to function as an electrical switch. Its main usages are the activation of lighting or alarms.

A motion sensor can work actively using electromagnetic waves (HF or Doppler radar) and ultrasonic (ultrasonic motion sensor) or passively using the infrared radiation of the surroundings – combinations are possible.

The most commonly used type of motion sensors is the PIR-Sensor (passive infrared) is. It reacts ideally towards angular changes, e.g. when someone passes the sensor.

Connections for limit switch

Limit switches (also called end switches or boundary sensors) are sensors that detect when a moved item (e.g. a work piece or a machine component) reached a certain position. The produced signal can be transmitted electrically, pneumatically or mechanically. Within sequence control systems in engineering that consist of several working steps, limit switches detect the end of a movement and thereby induce the next step of the process. They are also used as safety switches (e.g. door closed) to prevent human and mechanical damages.

System Overview

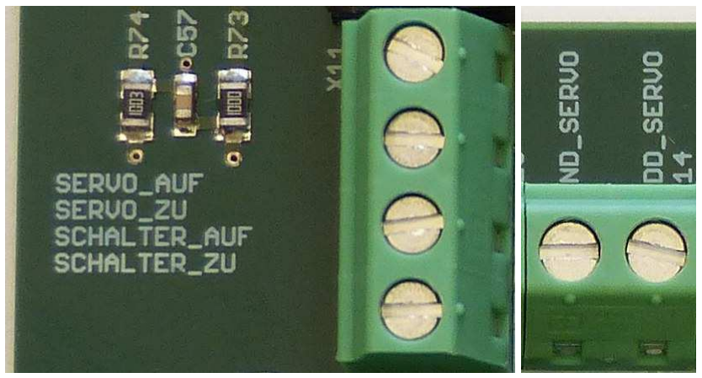
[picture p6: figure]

19.12.2017 | https://www.orn.mpg.de | Copyright 2017 ©, MPIO Seewiesen | page 11

Power supply for servomotor

Special electro motors enabling a control of their angular position as well as of their motor shaft and their speed of rotation are termed servomotors. They consist of an electromotor that is additionally equipped with a location determination sensor. The angular position of the motor shaft, detected by the sensor, gets continuously forwarded to an electronic control system - the so called servo controller, which is usually fixed outside of the actual motor. The servo controller then regulates the movement of the motor via a control circuit, corresponding to one or more adjustable set values like a set angular position, the shaft or the set rotation speed.

Connections for three RFID reading devices

RFID (radio-frequency identification) describes a technology for transceiver systems that uses automatic and non-contact identification and localisation of objects and living organisms with radio waves.

A RFID system consists of i) a transponder (sometimes referred to as radio tag) that is located on or within the object or living organism and contains an individual label and ii) a reading device for the readout of that label.

RFID transponders can be as small as a rice grain and implemented into e.g. pets or humans. Moreover, there is the possibility of producing the RFID transponders via a special printing technique of stable circuits made from polymers. The benefits of this technique emerge from the combination of a small size, an inconspicuous readout possibility (e.g. in the newly introduced ID card in Germany

System Overview

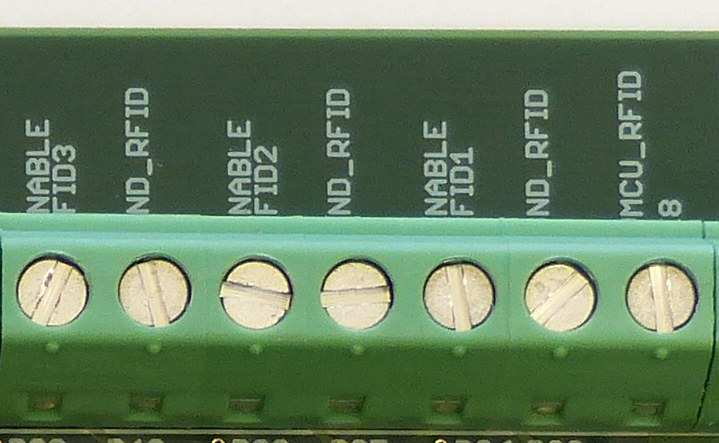
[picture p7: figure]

19.12.2017 | https://www.orn.mpg.de | Copyright 2017 ©, MPIO Seewiesen | page 12

on the 1st of November 2010) and the low price of the transponder (sometimes even cents). This new technique could potentially replace the nowadays commonly used barcode.

The coupling takes place through an – by the reading device created – alternating magnetic field in short range or via high frequency radio waves. Thereby data gets transferred and the transponder is provided with energy. For an attainment of longer ranges, active transponders with an in-built power supply are used, that, on the downside, come along with higher costs.

The reading device contains a software (a microprogram) that controls the actual reading process and a RFID middleware with digital interfaces for further EDV systems and databases, see RFID buses of the MOMO circuit board.

System Overview

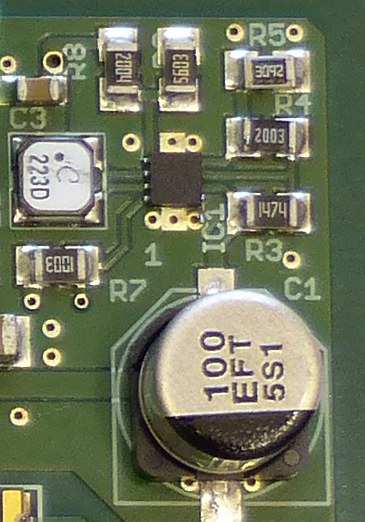
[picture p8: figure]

19.12.2017 | https://www.orn.mpg.de | Copyright 2017 ©, MPIO Seewiesen | page 13

Power supply for MOMO

The Texas Instruments TPS62125 3-17V down converter is a highly efficient device, optimized for applications with low and very low power drain of up to 300mA output current. The large input voltage range of 3V to 17V supports four alkali-cells and one to four LiP battery-cells in serial configuration as well as applications powered with 9V and 15V. The down converter TPS62125 owns a precise low-consumption comparator, which is used for input voltage control to meet system specific requirements during power on and off.

Debug Interface (DBG)

The debug interface software is stored on the microcontroller flash memory. Only after the flash memory contains this information, the hardware can be operated. The connection is either realised directly with a USB cable to the
debug interface or with a debugging probe. If
the connection is realized directly through the
USB cable only HEX files and BIN files can be transferred.

System Overview

19.12.2017 | https://www.orn.mpg.de | Copyright 2017 ©, MPIO Seewiesen | page 14

EFM32 Microcontroller

So called microcontroller (MCU) are flip chips that, at the same time, contain a processor and peripheral functions. In many MCUs, the internal and program memory are located partially or entirely on the same chip.

EFM32 is a family of microcontrollers offered by
Silicon | Laboratories. | The | EFM32 | are | 32-bit
microcontrollers of different sub-families that use ARM cortex-M3 processors. The energy consumption received special focus during the development, which
influenced naming: EFM stands for Energy Friendly
Microcontrollers. The low power demand makes the
EFM32 microcontroller especially suitable for applications with battery supply. EFM32 microcontroller contain several energy-saving modes that can be changed easily. Additionally, many peripheral devices can be plugged.

Within the Animal Presence RFID Data Logger the EFM32G230 microcontroller is used with 128 KB Flash Memory and 16 KB RAM Memory.

The EFM32 series is also known as “Gecko” by the developer, as these animals consume only 10% of the energy used by a mammal of similar size.

Energy Micro states that benchmark measurements with other leading energy saving MCU’s, found that the EFM32-MCU consumes only a quarter of the energy consumed by the other 8-, 16-, or 32-bit-MCU’s.

The EFM32 microcontroller based on the ARM Cortex processor is well suited for energy saving applications such as:

- electricity-, gas- and water-meters
- factory automation and building automation systems
- alarm and security technology as well as portable applications for medical

engineering or within the fitness sector.

The ARM Cortex-M3 processor is developed by Energy Micro and has been bought by Silicon Labs. Since the used processor works with 32 bit, data processing is much faster than 8 and 16 bit CPUs. Therefore, tasks are completed with less clock cycles, which reduces the dwell time in an active mode substantially.

System Overview

19.12.2017 | https://www.orn.mpg.de | Copyright 2017 ©, MPIO Seewiesen | page 15

The EFM32G230 contains an UART-interface for communication with external systems, which is especially designed for energy saving. The interface is referred to as LEUART-interface. LEUART is a serial interface, a kind of bus system. Through the LEUART-interface, a jack connector and a USB cable can be used to establish a connection to a computer.

Capacitor

A capacitor (German “Kondensator”) is a passive electric component with the ability to store electrical charge and electrical energy of a continuous circuit statically in an electrical field.

When the electrical power supply through the battery is
missing, the capacitor ensures an alternate power supply for the Multifunctional Mainboard to Observe and Manipulate Organisms (MOMO). The capacitor is charged when the accumulator supplies energy to the system. This allows energy to be obtained for a certain time from the capacitor if it is required.

Especially the clock of the microcontroller continuous to be powered when there is no external electrical power supply.

Some applications only become possible through double layered capacitors. Despite its large capacity, it is very small in size. The dielectric strength is not exceptionally high however, with only a few volts. Through its large capacity, the Gold Cap is present to maintain the power supply when the main energy source fails. In devices in which data storage should remain in switched off status, the Gold Cap is particularly well suited.

Life expectancy is limited from roughly 8 to 10 years. When the operating temperature is above optimal or the discharge current is high, the life expectancy and the capacity begin to decline over time. The Gold Cap most appropriate when it is rarely discharged and used with low currents.

System Overview

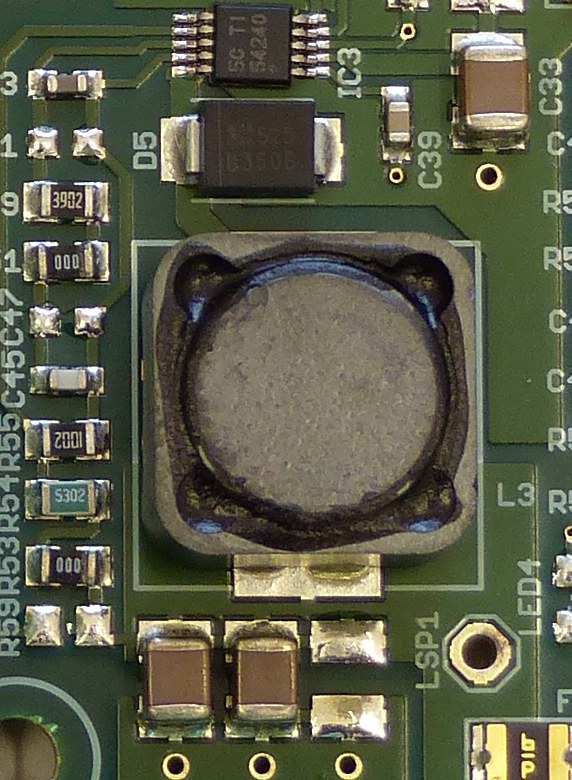
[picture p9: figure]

19.12.2017 | https://www.orn.mpg.de | Copyright 2017 ©, MPIO Seewiesen | page 16

Connecting terminal for the radio clock

See chapter 1.3

Output voltages (down converter)

The TPS62125 3.5V-42V down converter from Texas Instruments is a highly efficient converter, which is optimized for low and ultra-low power applications of up to 2.5 A output current. If no load is recognised by the controller, the standby current is 138 µA. The controller is run by MOMO in the Shutdown Mode. The Shutdown Current is 1.3 µA.

System Overview

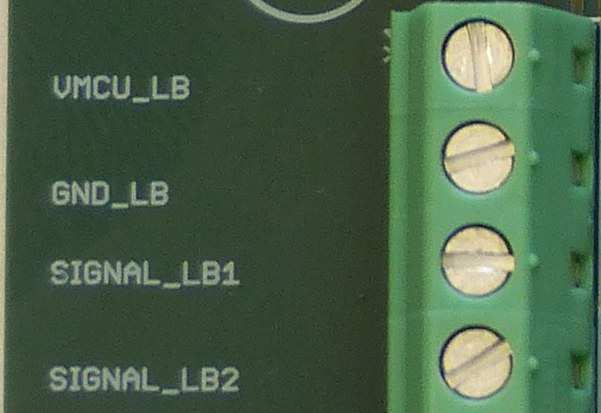
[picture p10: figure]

19.12.2017 | https://www.orn.mpg.de | Copyright 2017 ©, MPIO Seewiesen | page 17

Power supply for light barrier

A light barrier is an optoelectronic system, which indicates an interruption in the beam of light and communicates this event via an
electrical | signal. | This | way, | automatic
devices can detect moving objects without contact. Examples are the detection of obstacles in autonomously closing doors or of invaders via alarm systems.

SMBus „System Management Bus“

MOMO supports following standard communication bus systems:

SMBus „System Management Bus“ (http://www.smbus.org/) as well as the
I²C „Inter-Integrated Circuit Interface“ below a frequency of 100 kHz. https://en.wikipedia.org/wiki/I%C2%B2C

The System Management Bus (SMBus) is
needed for the communication between MOMO and the microcontroller with ‘Battery management system’ (BMS).
For reading the single registers of the microcontroller with BMS via the SMBus, the software commands ‘SBS Commands’ were installed.

System Overview

19.12.2017 | https://www.orn.mpg.de | Copyright 2017 ©, MPIO Seewiesen | page 18

Jack connector as interface to a PC

For the development of the Multifunctional Mainboard to Observe and Manipulate Organisms an Interface for connection to a computer is intended. Through the data communication interface LEUART, which is provided by the microcontroller EFM32G230 out of chapter 1.2.10. The jack
connector is used to connect the signal of the
LEUART interface with a PC. For this, a jack
connector with 3.5 mm, found in many audio applications, is applied. Please regard a power supply of 3.3 V when buying cables.

LEDs

There are two built-in LED’s. The yellow LED (LED 2) indicates, that something is written on the SD card. If the red LED (LED 1) flashes, it indicates that the radio time gets received. If the LED 1 blinks longer than 5 minutes or flashes continuously, this indicates a malfunction.

SD Memory Card Connector

The data from the RAM memory is stored in form of *.txt files on the SD-card, this is located in the SD Memory Card Connector. The size of the memory influences the energy consumption; the smaller the memory size is, the smaller the energy consumption. Therefore, it is recommended for the Multifunctional Mainboard to Observe and Manipulate Organisms
(MOMO) to use a small SD memory size of 2 GB.
Larger memory sizes increase MOMOs Energy
consumption. Memory sizes are supported from 2 GB to 32 GB. Not every event is written onto the SD card immediately. It is first waited for the provided memory to be full. The writing on the SD card consumes quite some energy, which is why the access to the SD card should occur as rare as possible.

System Overview

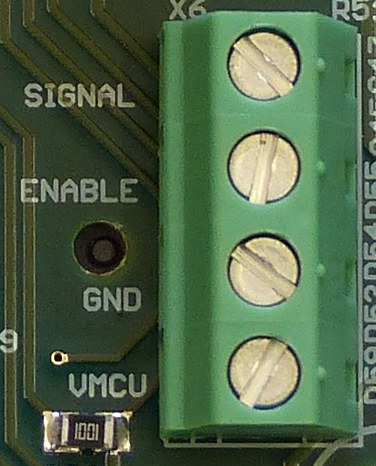
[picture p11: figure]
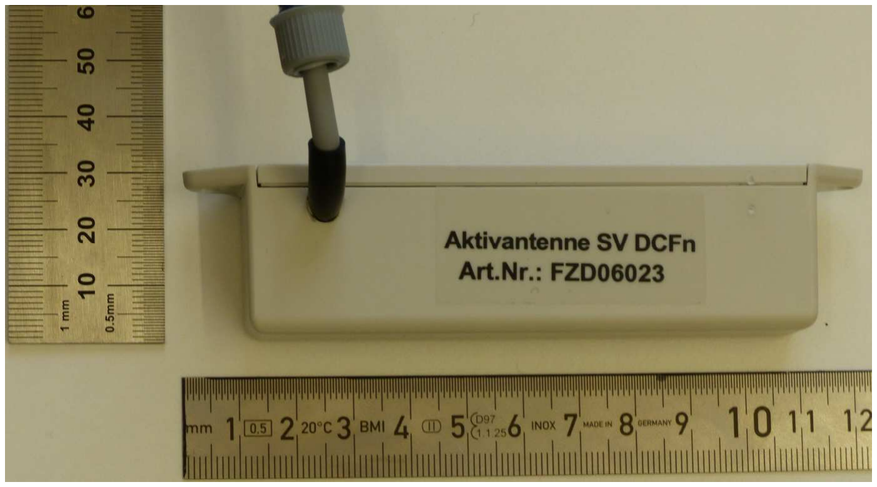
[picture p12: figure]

19.12.2017 | https://www.orn.mpg.de | Copyright 2017 ©, MPIO Seewiesen | page 19

## System configuration radio clock receiver

Connector

Hardware illustration

System Overview

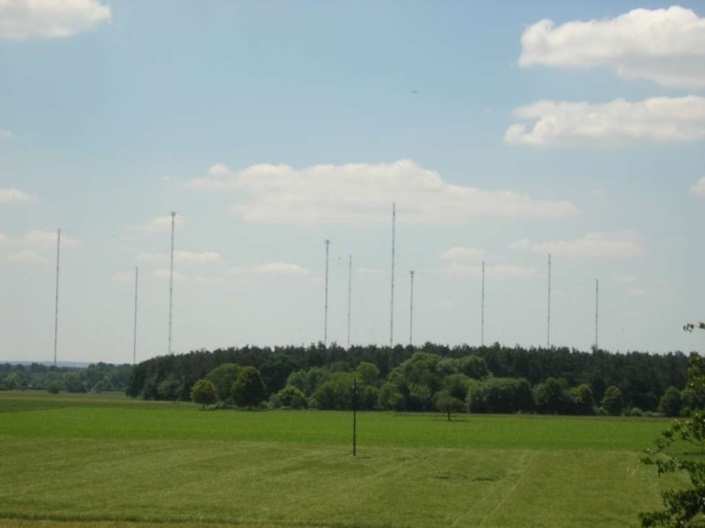
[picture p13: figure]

19.12.2017 | https://www.orn.mpg.de | Copyright 2017 ©, MPIO Seewiesen | page 20

Radio clock

The current version of the Smart Feeder features a radio clock, which works in a similar way as a normal clock. In periodic intervals a signal to Europe from the long wave antenna in Mainflingen with a frequency of 77.5 kHz is received and synchronized. Long wave signals have been compared to short waves and medium waves, and have a relatively high range, making it is possible to receive the signal from Mainflingen with a range of up to 2000 km. On other continents, the time signals can be received as well, though with different frequencies.

The time of the radio clock is prompted every 24 hours by default and gets transferred to the clock of the MCU. A non-standard detection takes place during a reset of the system or after energy supply has been restored, after the capacitor was discharged for too long to bridge power supply and in case of the voltage to come below 1.8 V.

The power supply of the clock is driven
by an accumulator, which is also used for the other electric consumers and is described in chapter 1.7.
countries | designation | frequency
Germany | DCF | 77.5 kHz
France | TDF | 162 kHz
China | BPC | 68.5 kHz
Japan | JJY | 40 and 60 kHz
USA | WWVB | 60 kHz
Russia | Beta | 25 kHz
Great Britain | MSF | 60 kHz

Smart Feeder (Hardware)

19.12.2017 | https://www.orn.mpg.de | Copyright 2017 ©, MPIO Seewiesen | page 21

## Smart Feeder (Hardware)

Peripheral devices are essential for the regular operation of the Multifunctional Mainboard to Observe and Manipulate Organisms. Concerning the Smart Feeder application these include an accumulator, a radio clock receiver, a light barrier board with a light barrier, a RFID reader and a servomotor board with a servomotor.

Hardware illustration Smart Feeder

Smart Feeder (Hardware)

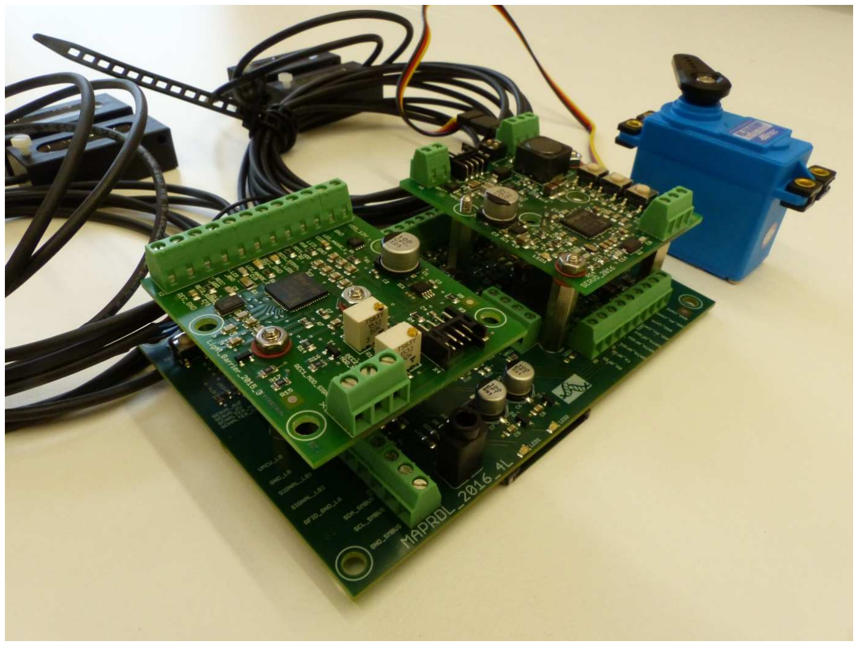
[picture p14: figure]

19.12.2017 | https://www.orn.mpg.de | Copyright 2017 ©, MPIO Seewiesen | page 22

Required boards:

MAPRDL_2016_4L, light barrier actuator, servomotor actuator

Smart Feeder (Hardware)

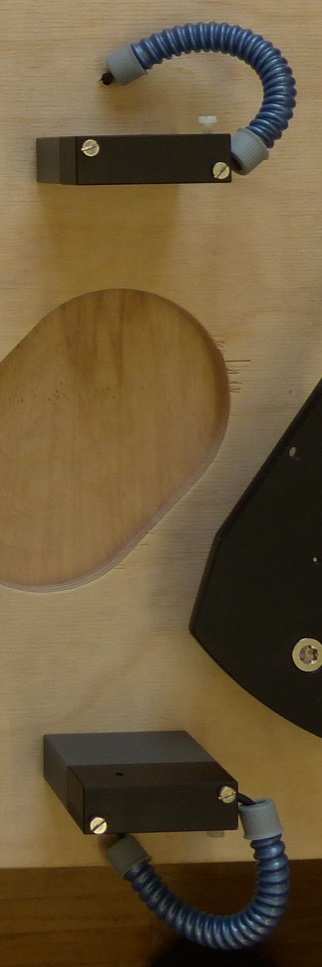
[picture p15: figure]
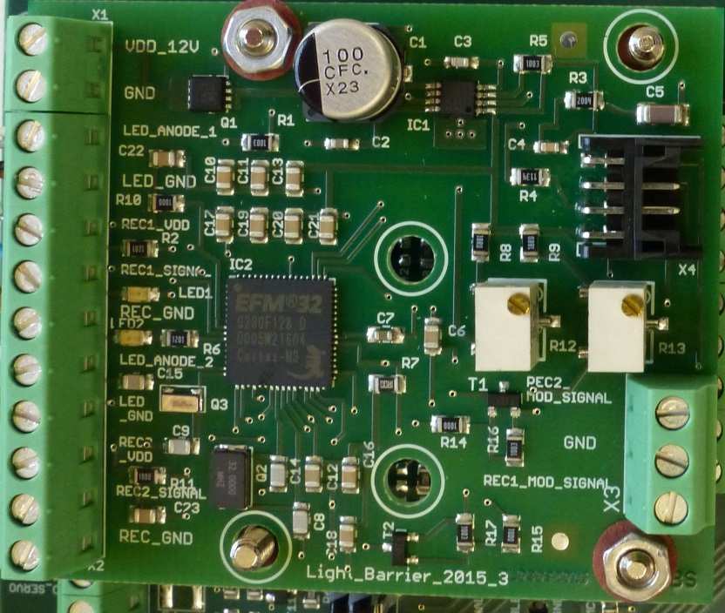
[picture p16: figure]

19.12.2017 | https://www.orn.mpg.de | Copyright 2017 ©, MPIO Seewiesen | page 23

Light barriers

In optoelectronics, a light barrier is system, which indicates an interruption in the beam of light and communicates this event through an electrical signal. Light barriers are composed of a beam source (transmitter) and a photodiode (emitter) to receive the beam.

In the Smart Feeder application, the interruption of an animal is solely detected with light barriers. A maximum of two light barriers can be scanned with up to 100 Hz. The current drain is <120 µA (calculated amount) with a sampling of 10 Hz.

The detection of an object between the light barrier commands an activation of the RFID reader. This needs to occur in a relatively short time, as birds often move quickly. If signal transmission is slower, the RFID reader cannot receive the transponder signal from the bird, because the bird may already be out of range.

The light barriers work with adaptive selectivity, which
means that pollution of the transmitter and emitter, aging or fluctuations due to temperature can be largely compensated for. This reduces the possibility of false detections for example through sunlight.

The required low-power light barrier actuator.

Smart Feeder (Hardware)

19.12.2017 | https://www.orn.mpg.de | Copyright 2017 ©, MPIO Seewiesen | page 24

RFID Reader for transponders

RFID (radio-frequency identification) describes a technology for transceiver systems that uses automatic and non-contact identification and localisation of objects and living organisms with radio waves.

A RFID system consists of a transponder that is located on or within the object or living organism and contains an individual label and a reading device with an antenna for the readout
of that label.

The coupling takes place via alternating magnetic fields produced by the reader within short range or via high frequency radio waves. Thereby, not only data is transmitted, but the transponder is also supplied with energy. Active transponders with a local power source are used to achieve longer ranges, but come along with higher expenses.

RFID’s are also used in other areas such as electronic locks, ski passes, cashless payment transactions, electronic immobilizers and in libraries as theft protection.

The transponder frequency is not exactly the same as the RFID reader frequency. The RFID Reader works with a frequency of 125 kHz and the transponder with 134.2 kHz. However, both systems are compatible and function together.

### 2.1.3.1 RFID receiver module

A RFID receiver module with a frequency of 125 kHz is used in the Smart Feeder application. The used receiver module from Elatec is designed with a small size, small price and versatile applications.

Smart Feeder (Hardware)

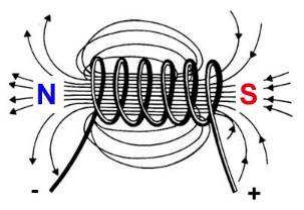
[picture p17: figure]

19.12.2017 | https://www.orn.mpg.de | Copyright 2017 ©, MPIO Seewiesen | page 25

### 2.1.3.2 RFID antenna

The used RFID antenna has a diameter of 50 mm and is directly soldered on the RFID receiver module. If a voltage source is connected to the antenna, which is an air core coil with an inductivity of 490 µH and current begins to flow, an electric field is generated. The electric field is the energy source for the transponder.

If a transponder with its own antenna transmits a signal at a certain frequency, the RFID reader’s antenna collects the signal and transmits it.

### 2.1.3.3 RFID Transponder

The used transponder is the highest performing passive transponder currently available on the market.
These transponders are encapsulated in biocompatible
glass and provide 100% unique identification. Because
of the small size of 8 mm x 1.4 mm and a very low weight of only 30 mg the tagged animals are minimally affected. So it is possible to tag even very small animals such as red ants

The transponder contains a non-volatile flash memory. A combination of letters and numbers is stored on the flash memory during the production of the transponder.

Smart Feeder (Hardware)

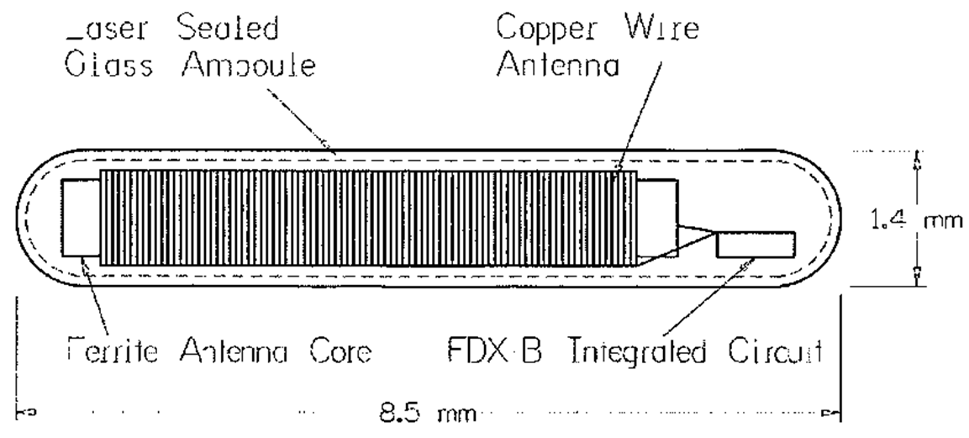
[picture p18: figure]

19.12.2017 | https://www.orn.mpg.de | Copyright 2017 ©, MPIO Seewiesen | page 26
The | transponders | are | known | as | FDX-B
MINIHPT8 and are made by the company Biomark. The FDX-B indicates that the full duplex technique is used.

In duplex mode operating systems the electric
field is always present and the transponder sends its signal as soon as it enters the reception area of the reader. The FDX transponder sends its ID continuously and can therefore be received relatively rapid.

Smart Feeder (Hardware)

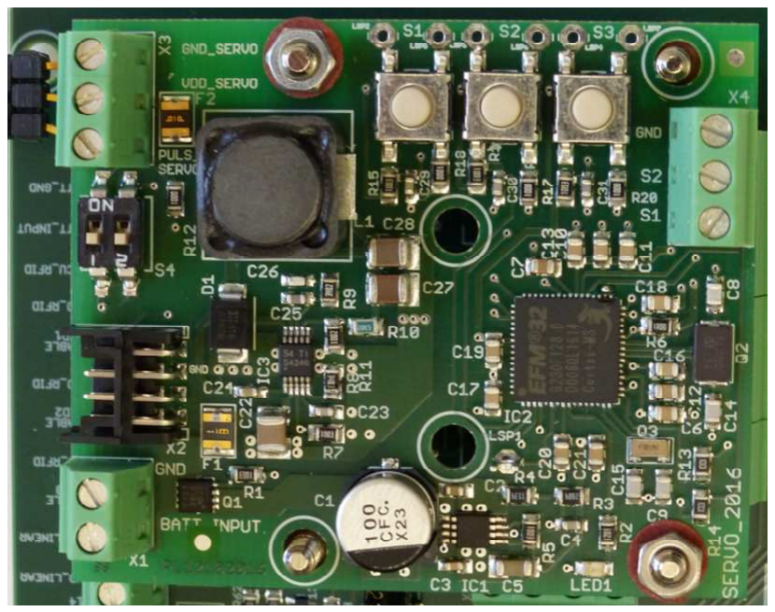
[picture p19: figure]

19.12.2017 | https://www.orn.mpg.de | Copyright 2017 ©, MPIO Seewiesen | page 27

## Servomotor

Food flap | Servomotor HITEC HS-5646WP

The low-power servomotor actuator can be programed manually via the 3 switches. The final positions ‘food flap open’ and ‘food flap closed’ can be set and the processing speed of the flap can be adjusted.

The required low-power servomotor actuator.

Smart Feeder (Hardware)

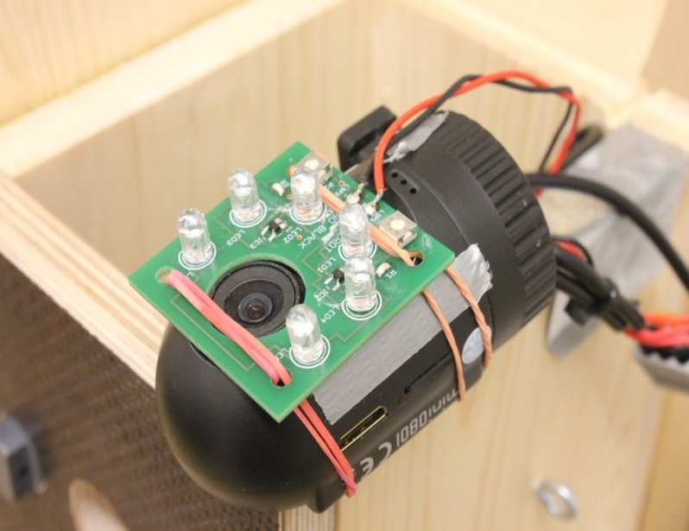
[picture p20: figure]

19.12.2017 | https://www.orn.mpg.de | Copyright 2017 ©, MPIO Seewiesen | page 28

## Dashcam

Video recording device with 12 V battery terminal.

Housing for camera | Full HD Car DVR with GPS

Smart Feeder (Hardware)

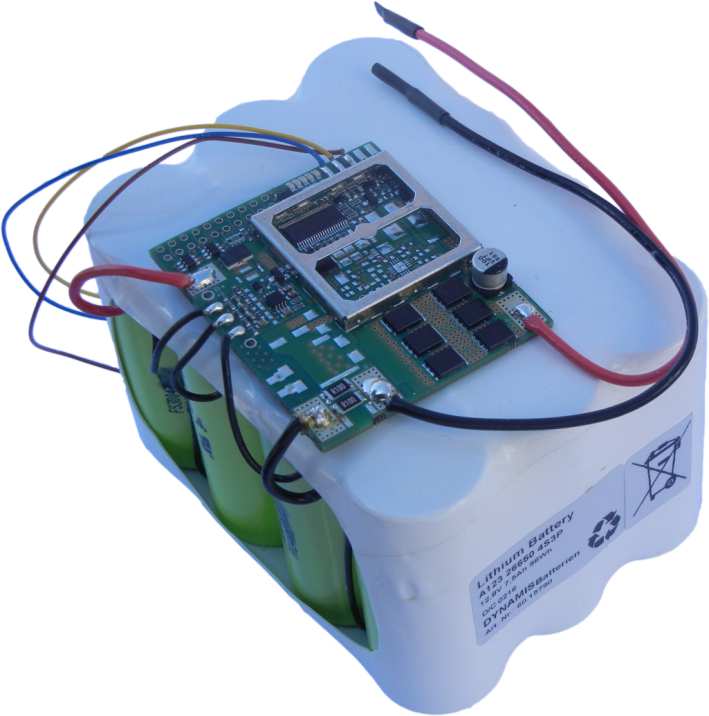
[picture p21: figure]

19.12.2017 | https://www.orn.mpg.de | Copyright 2017 ©, MPIO Seewiesen | page 29

## Accumulator

The lithium-ion battery from the
company | Dynamis | Batterien
supplies Multifunctional Mainboard
to | Observe | and | Manipulate
Organisms (MOMO) with electrical energy. The capacity was chosen to ensure that there is enough energy to supply the Smart Feeder in a very active period for two weeks. Through the little specific energy of the lithium-ion battery of
approximately | 108 Wh/kg, | the
change of the accumulators is much less energy-sapping than with lead-acid batteries with a specific energy of 30 - 60 Wh/kg.

The three LED’s on the accumulator’s board indicates the state of charge. One lit LED indicates that the accumulator is fully charged. Two LED’s indicate the accumulator is halfway charged. Three LED’s indicate an almost empty state of charge

The lithium-ion battery has its own board, which can communicate with MOMO via a bus system. Currently, the temperature of the accumulator, the capacitance values and the latest current drain of the Smart Feeder are prompted from MOMO.

Smart Feeder (Hardware)

19.12.2017 | https://www.orn.mpg.de | Copyright 2017 ©, MPIO Seewiesen | page 30

## Pin assignment and connectors

Pin allocation

### 2.5.1.1 Peripheral terminal

connection | designation | cable colour
X1-2 | BATT_INPUT | red (battery pack)
X1-1 | BATT_GND | brown (battery pack)
connection | designation
X2-1 | VMCU
X2-2 | SWDIO
X2-3: | GND
X2-4 | SWCLK
X2-5 | GND
X2-6: | SWO
X2-7 | frei
X2-8 | MCU_RESET

Smart Feeder (Hardware)

19.12.2017 | https://www.orn.mpg.de | Copyright 2017 ©, MPIO Seewiesen | page 31
connection | designation | cable colour
X3-6 | SIGNAL_PIR2
X3-5 | SIGNAL_PIR1 | red/white LB
X3-4 | GND_PIR2
X3-3 | GND_PIR1
X3-2 | VMCU_PIR2
X3-1 | VMCU_PIR1
connection | designation | cable colour
X4-1 | VMCU_LB | white (RFID)
X4-2 | GND_LB
X4-3 | SIGNAL_LB1
X4-4 | SIGNAL_LB2
X4-5 | RFID_GND_LB | brown (RFID)
connection | designation | cable colour
X5-1 | SDA_SMBUS | blue
X5-2 | SCL_SMBUS | yellow
X5-3 | GND_SMBUS | grey

Smart Feeder (Hardware)

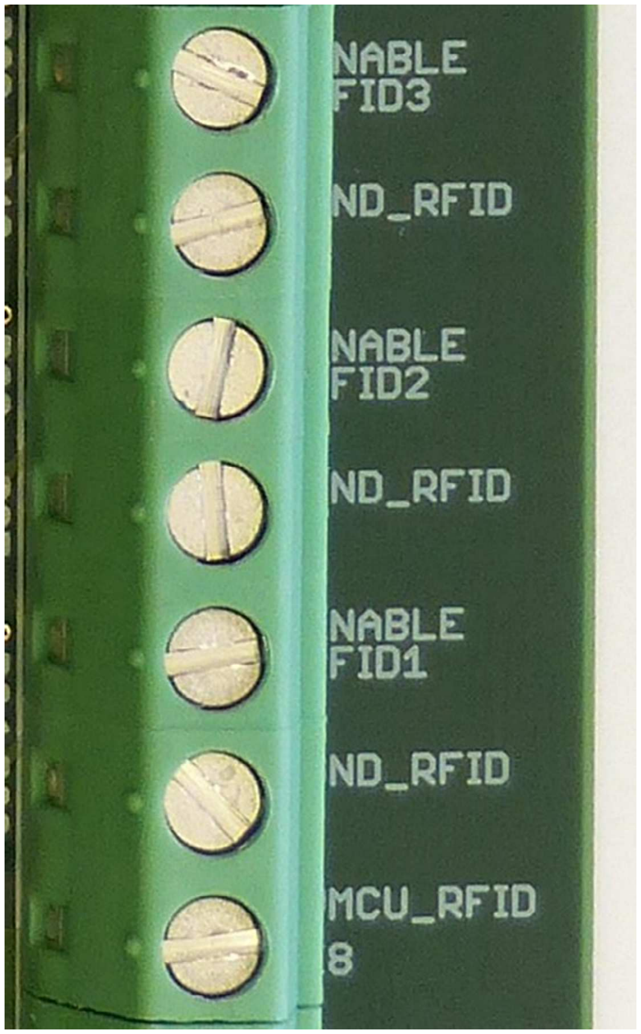
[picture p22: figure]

19.12.2017 | https://www.orn.mpg.de | Copyright 2017 ©, MPIO Seewiesen | page 32
connection | designation | cable colour
X6-1 | DCF_SIGNAL | green
X8-6 | DCF_ENABLE | yellow
X8-5 | DCF_GND | brown
X8-4 | DCF_VMCU | white
connection | designation
X7-1 | DATA_RFID1
X7-2 | DATA_RFID2
X7-3 | DATA_RFID3
connection | designation | cable colour
X8-7 | ENABLE_RFID3
X8-6 | GND_RFID
X8-5 | ENABLE_RFID2
X8-4 | GND_RFID
X8-3 | ENABLE_RFID1
X8-2 | GND_RFID
X8-1 | VMCU_RFID

Smart Feeder (Hardware)

19.12.2017 | https://www.orn.mpg.de | Copyright 2017 ©, MPIO Seewiesen | page 33
connection | designation | cable colour
X9-1 | RX_RFID | grey
X9-2 | TX_RFID | pink
connection | designation | cable colour
X10-1 | VDD_5V_CAM1 | red
X10-2 | GND_CAM1 | black
X10-3 | VDD_5V_CAM2
X10-4 | GND_CAM2
connection | designation | cable colour
X11-1 | SERVO_AUF | red/white
X11-2 | SERVO_ZU | red/white
X11-3 | SCHALTER_AUF
X11-4 | SCHALTER_AUF
connection | designation | cable colour
X12-4 | LINEAR_I_AB
X12-3 | LINEAR_CLK
X12-2 | LINEAR_DIR
X12-1 | LINEAR_ENABLE

Smart Feeder (Hardware)

19.12.2017 | https://www.orn.mpg.de | Copyright 2017 ©, MPIO Seewiesen | page 34

### 2.5.1.2 Jack connectors for LEUART

connection | designation | cable colour
X13-2 | SCHALTER_ZU
X13-1 | SCHALTER_AUF
connection | designation | cable colour
X14-2 | GND_SERVO
X14-1 | VDD_SERVO
connection | designation | cable colour
X15-2 | GND_LINEAR
X15-1 | VDD_LINEAR
connection | designation
J1 | LEUART_RX
J1 | LEUART_TX

Smart Feeder (Hardware)

19.12.2017 | https://www.orn.mpg.de | Copyright 2017 ©, MPIO Seewiesen | page 35

Technical description of additional connectivity options for applications

PA3_CAM1_ENABLE; VDD_5V_CAM1:
Input Voltage Range: 3.5V-11V@2.5A

Applications: recorder, sound player, camera system, animal transponder reader, scale, heater element, cooling element, DC motors, light (infrared, LEDs), temperature sensor, humidity sensor, brightness sensor, motion sensor, light barriers, infrared sensor. Global System for Mobile Communications (GSM), Bluetooth

PA4_CAM2_ENABLE; VDD_5V_CAM2:
Input Voltage Range: 3.5V-11V@2.5A

Applications: recorder, sound player, camera system, animal transponder reader, scale, heater element, cooling element, DC motors, light (infrared, LEDs), temperature sensor, humidity sensor, brightness sensor, motion sensor, light barriers, infrared sensor. Global System for Mobile Communications (GSM), Bluetooth

PA6_RFID_POWER; RFID_GND_LB:
Electrically switchable mass: Input Voltage Range from Circuit: 3.3V@0.22A

Applications: animal transponder reader, heater element, cooling element, motors, light, temperature sensor, humidity sensor, brightness sensor, motion sensor, light barriers, infrared sensor.

PA8_RFID1_DATA:

Device Pinout: TIM2_CC0 #0

The TIMER (Timer/Counter) keeps track of timing and counts events, generates output waveforms and triggers timed actions in other peripherals.

Applications: animal transponder reader, servomotor, counter.

Smart Feeder (Hardware)

19.12.2017 | https://www.orn.mpg.de | Copyright 2017 ©, MPIO Seewiesen | page 36

PA9_RFID2_DATA:

Device Pinout: TIM2_CC1 #0

The TIMER (Timer/Counter) keeps track of timing and counts events, generates output waveforms and triggers timed actions in other peripherals.

Applications: animal transponder reader, servomotor, counter.

PA10_RFID3_DATA:

Device Pinout: TIM2_CC2 #0

The TIMER (Timer/Counter) keeps track of timing and counts events, generates output waveforms and triggers timed actions in other peripherals.

Applications: animal transponder reader, servomotor, counter.

PB12_N_SCHALTER_ZU:
Device Pinout: DAC0_OUT1 #0, LETIM0_OUT1 #1

The DAC is designed for low energy consumption, but can also provide very good performance. It can convert digital values to analog signals at up to 500 kilo samples/second and with 12-bit accuracy.

The LETIMER is a down-counter that can keep track of time and output configurable waveforms. Running on a 32.768 kHz clock the LETIMER is available even in EM2 with sub μA current consumption.

PC0_RFID_RX:
Device Pinout: ACMP0_CH0 #0, PCNT0_S0IN #2, US1_TX #0

The ACMP (Analog Comparator) compares two analog signals and returns a digital value telling which is greater.

The Pulse Counter (PCNT) decodes incoming pulses. The module has a quadrature mode which may be used to decode the speed and direction of a mechanical shaft. PCNT can operate in EM0-EM3.

The USART handles high-speed UART, SPIbus, SmartCards, and IrDA communication.

Smart Feeder (Hardware)

19.12.2017 | https://www.orn.mpg.de | Copyright 2017 ©, MPIO Seewiesen | page 37

PC1_RFID_TX:
Device Pinout: ACMP0_CH1 #0, PCNT0_S1IN #2, US1_RX #0

The ACMP (Analog Comparator) compares two analog signals and returns a digital value telling which is greater.

The Pulse Counter (PCNT) decodes incoming pulses. The module has a quadrature mode which may be used to decode the speed and direction of a mechanical shaft. PCNT can operate in EM0-EM3.

The USART handles high-speed UART, SPIbus, SmartCards, and IrDA communication.

PC8_RFID1_MOSFET, VDD_RFID1:
Input Voltage Range from Circuit: 3.3V@0.2A

Applications: recorder, sound player, camera system, animal transponder reader, scale, heater element, cooling element, DC motors, light (infrared, LEDs), temperature sensor, humidity sensor, brightness sensor, motion sensor, light barriers, infrared sensor. Global System for Mobile Communications (GSM), Bluetooth

PC9_RFID2_MOSFET, VDD_RFID2:
Input Voltage Range from Circuit: 3.3V@0.2A

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

PC10_RFID3_MOSFET, VDD_RFID3:
Input Voltage Range from Circuit: 3.3V@0.2A

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

Smart Feeder (Hardware)

19.12.2017 | https://www.orn.mpg.de | Copyright 2017 ©, MPIO Seewiesen | page 38

PC11_LINEAR_ENABLE:
Device Pinout: ACMP1_CH3 #0, US0_TX #2

The ACMP (Analog Comparator) compares two analog signals and returns a digital value telling which is greater.

The USART handles high-speed UART, SPIbus, SmartCards, and IrDA communication.

PC13_LINEAR_CLK:
Device Pinout: ACMP1_CH5 #0, TIM0_CDTI0 #1/3 TIM1_CC0 #0 PCNT0_S0IN #0

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

The Pulse Counter (PCNT) decodes incoming pulses. The module has a quadrature mode which may be used to decode the speed and direction of a mechanical shaft. PCNT can operate in EM0- EM3.

Smart Feeder (Hardware)

19.12.2017 | https://www.orn.mpg.de | Copyright 2017 ©, MPIO Seewiesen | page 39

## Housing

Housing for the main board

The housing from the main board consists entirely of opaque polycarbonate. The lid is lockable with bayonet locks which are quick and easy to use. The screws are secured from falling out and prevents loss of any screws.

Smart Feeder (Hardware)

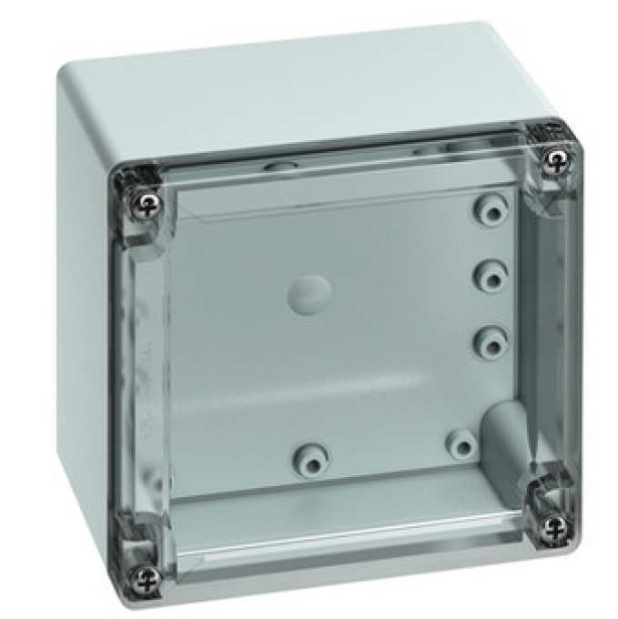
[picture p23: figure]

19.12.2017 | https://www.orn.mpg.de | Copyright 2017 ©, MPIO Seewiesen | page 40

Housing for the accumulator

The housing from the accumulator consists entirely of polycarbonate, with the lid being made from transparent polycarbonate so the LED’s inside may be seen without needing to open the lid. The lid is also lockable with bayonet locks. The same screws are used here and are also secured against falling out.

General working conditions

19.12.2017 | https://www.orn.mpg.de | Copyright 2017 ©, MPIO Seewiesen | page 41

## General working conditions

Component designation | Multifunctional Mainboard to Observe and Manipulate Organisms Smart Feeder Application
Manufacturer | MPIO http://www.orn.mpg.de/
Dimensions main board (L X B x H) | 121 mm x 81 mm x 1,5 mm
Overall temperature range | -10°C to 70°C (DCF77)
Storage temperature range | -20°C to 60°C
Overall moisture | Relative moisture 35% to 85% (at 5 to 35°C)

Detailed information, in particular concerning the electrical properties of the Multifunctional Mainboard to Observe and Manipulate Organisms can be found in the datasheet.

The working conditions from single devices can be found in the datasheets in chapter 8.

Energy supply

19.12.2017 | https://www.orn.mpg.de | Copyright 2017 ©, MPIO Seewiesen | page 42

## Energy supply

The Multifunctional Mainboard to Observe and Manipulate Organisms (MOMO) is especially designed to have low energy requirements. The electrical power requirements are explained more precisely in this chapter.

The EFM32G230 has five different economical energy modes, where only two of which are used for MOMO. These are the Deep Sleep Mode and the Sleep Mode whereby the Sleep Mode is the Active Mode and the Deep Sleep Mode is the Inactive Mode. In these energy modes different consumers are active. The Smart Feeder application of the Multifunctional Mainboard to Observe and Manipulate Organisms switches between the Active Mode and the Inactive Mode through light barrier activity. If the RFID reader and the light barrier detect no activity for 6 minutes, the Smart Feeder switches into the Inactive Mode again to save energy.

The energy-intensive consumers, like the RFID reader, are only supplied with electrical Energy when required. The RFID reader is the largest consumer of electrical energy in the Smart Feeder application, when no camera is connected.

Electrical properties and, to some extent, battery drain, can be drawn from the datasheets of the built-in components. The datasheets are linked in chapter 8.

In the following sections, the current supply and the voltage supply will be exam-ined separately.

Energy supply

19.12.2017 | https://www.orn.mpg.de | Copyright 2017 ©, MPIO Seewiesen | page 43

## Current supply

ARM Cortex Processor

From the five available modes of operation only the Deep Sleep Mode and the Sleep Mode are used.

### 0.9 μA @ 3 V Deep Sleep Mode, including Real Time Clock with 32.768 kHz

Oscillator, Power-on Reset, Brown-out Detector, RAM and CPU retention

### 45 μA/MHz @ 3 V Sleep Mode

RFID

RFID on measured: 35,4mA

RFID off measured: 1,36mA

(from schematics)

Light barriers

The light barriers are always supplied with electricity, independently from the two energy modes. To save energy, the status of the light barrier is not assessed continuously but 100 times per second, thus with a frequency of 100 Hz. Therefore, the light barrier has a very small electrical energy demand of roughly 120 µA.

Radio clock

The clock of the microcontroller is updated at a certain time every night through the time signal from Mainflingen. The radio time will be also updated when the system is reset.

Nominal current 100µA | Quiescent current 5 µA

LED

Each LED has an electric current demand of 2 m. There are two built-in LEDs.

Energy supply

19.12.2017 | https://www.orn.mpg.de | Copyright 2017 ©, MPIO Seewiesen | page 44

Accumulator LED’s and self-discharge

LEDs | electric current demand
Without | 271 µA
Only LED1 | 308 µA
LED1 + LED2 | 343 µA
LED1 + LED2 + LED3 | 384 µA

The self-discharge by lithium-ion-batteries at 20°C is less than 2% per month.

Overview of the nominal currents

This table contains the maximum current demands of the most important devices. If all are active at the same time, the current demand behind the down converter at 3,3 V is 51 mA and with that the maximum power input before the down converter is around 0,1683 W.

devices | currents
RFID | 35.4 mA
2* LED | 2 x 2 mA
ARM Cortex M3 | 45 µA/MHz (1.44 mA)
radio clock | 0.1 mA
light barriers | 2x 120 µA
Total current behind the down converter with 3.3V | 42.2 mA (When all consumers are active at the same time without down converter losses)
Total input in front of the down converter with 12.8 V | 155 mW (When all consumers are active at the same time with down converter losses)

Energy supply

19.12.2017 | https://www.orn.mpg.de | Copyright 2017 ©, MPIO Seewiesen | page 45

Overview of the currents in the different operating modes

| Shutoff Mode | Stop Mode | Deep Sleep Mode | Sleep Mode | Run Mode
RFID | Not used | Not used | Off | Can be on | Not used
ARM Cortex M3 | Not used | Not used | On | On | Not used
Radio clock | Not used | Not used | Can be on | Can be on | Not used
LED’s | Not used | Not used | Can be on | Can be on | Not used
Light barrier | Not used | Not used | On | On | Not used
Down converter | Not used | Not used | On | On | Not used
Accumulator board | Not used | Not used | On | On | Not used

Energy supply

19.12.2017 | https://www.orn.mpg.de | Copyright 2017 ©, MPIO Seewiesen | page 46
| Deep Sleep Mode (inactive mode) | Sleep Mode (active mode)
RFID (with 3.3 V) | 0 | On (35.4mA)
ARM Cortex M3 (with 3.3 V) | 0,9 µA | 45 µA/MHz (1.44 mA)
Radio clock (with 3.3 V) | 0,1 mA (once a day for approx. 5 min; also at reset and start) | 0,1 mA (once a day for approx. 5 min; also at reset and start)
LED (with 3.3 V) | 2 mA (2 units if on) | 2 mA (2 units if on)
Light barrier (with 3.3 V) | 240 µA (2 units) | 30 µA (2 units)
Down converter (3.3 V) | 13 μA | 13 μA
Total current behind the down converter (without down converter losses and 3.3 V) | 0.0609 mA (2 x light barriers and und MCU | 36.88 mA (RFID active, MCU active, light barriers, down converter)
Total input behind of the down converter (without down converter losses and 3.3 V) | 0.0609 mA x 3.3 V = 0.000201 W = 201 x 10^-6 W | 36.88 mA x 3.3 V = 0.122 W
Total input in front of the down con-verter (with down converter losses and 12.8 V) | (with η = 50%) 0.000201W/0.5 = 0.000402 W = 402 x 10^6 W | (with η = 90%) 0.122 /0.9 = 0.136 W
Total current in front of the down converter (with down converter losses 12.8 V) (theoretical) | (with η = 50%) 0.0314 mA | (with η = 90%) 10.6 mA
Measured total current in front of the down converter (with down converter losses 12.8 V) (real) | 0.22 mA = real measured inactive mode (connected radio clock but inactive, controller in Deep Sleep Mode, Gold Cap, connected LED but off, buttons, down converter) | 11 mA = real measured active mode (connected radio clock but inactive, controller, LED connected but off, gold cap, SD card, down converter, light barrier, RFID on)
Accumulator board with LED‘s current demand | (0.271 mA – 0.384 mA) | (0.271 mA – 0.384 mA)
Total current with accumulator board | 0.3024 mA – 0.4154 mA | 10.87 mA – 10.98 mA
Total Input ink. accumulator board with 12.8 V (theoretical) | 0.00387 W – 0.00532 W | 0.139 W – 0.141 W
Total Input with measured value + theoretically accumulator board de-mand with 12.8 V (real) | 0.028 W – 0.0158 W | 0.141 W – 0.142 W

Energy supply

19.12.2017 | https://www.orn.mpg.de | Copyright 2017 ©, MPIO Seewiesen | page 47

## Voltage supply

All consumers are supplied with 3.5 Volts, which are provided by the down converter from the 12.8 Volts from the lithium-ion-accumulator. An input voltage of 5 V for the down converter is sufficient.

## Electrical energy storage

The main power supply is ensured by the lithium-ion-accumulator. If the accumulator is removed, a capacitor ensures the supply.

Accumulator

If the whole capacity of a lithium-ion-accumulator is completely used it can have negative effects on the lifetime of the accumulator. Therefore, a certain percent-age of the total capacity is not used. The accumulator of the Animal Presence RFID Data Logger uses 83% of the total capacity.

Roughly 17 % of the capacity of the accumulator are not used.

voltage | 12.8 V
Nominal capacity | 7.5 Ah
Total capacity | 8.97 Ah
stored energy | 96 Wh

The lithium-ion-accumulator has its own board, which is able to communicate with the Animal Presence RFID Data Reader via a data bus.

Capacitor

If the energy supply from the accumulator is no longer available, a capacitor with

### 0.22 farad ensures the energy supply. The stored energy is enough to supply

MOMO for around 30 seconds. During the discharge, the voltage of the capacitor declines from 3.6 Volts to 1.8 Volts.

Energy supply

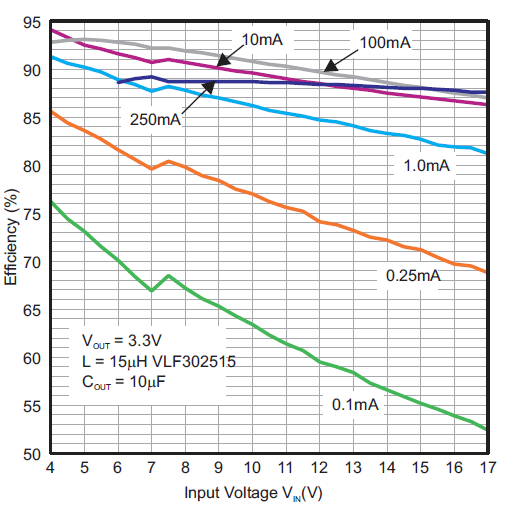
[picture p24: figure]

19.12.2017 | https://www.orn.mpg.de | Copyright 2017 ©, MPIO Seewiesen | page 48

Conversion losses

The accumulator provides electrical energy with a voltage of 12.8 Volts. The EFM32G230 and other consumers require a significantly smaller voltage of around 3.3 Volts. This reduction of voltage is achieved by a down converter which is described in chapter Fehler! Verweisquelle konnte nicht gefunden werden.. The down converter doesn’t work with transformers but with resistors.

Range estimation of the accumulator

Range at maximum power (If the Multifunctional Mainboard to Observe and Manipulate Organisms is always active and there is no maintenance, RFID) | 96 Wh / 0.142 W = 676 hours = 28.16 days
Range at minimum power (The Multifunctional Mainboard to Observe and Manipulate Organisms is in the Deep Sleep Mode and there is no maintenance; radio clock and RFID off, 1x light barrier) | 96 Wh / 0.0058 W = 16552 hours = 690 days = 1.889 years

The value for the range at minimum power can only theoretically be achieved. In reality the self-discharge causes the accumulator to be discharged earlier. Moreover, an inactivity of more than two years is not intended for the application.

Operation of the Smart Feeder

19.12.2017 | https://www.orn.mpg.de | Copyright 2017 ©, MPIO Seewiesen | page 49

## Operation of the Smart Feeder

The operation of the Multifunctional Mainboard to Observe and Manipulate Organisms (MOMO) with the Smart Feeder application will be explained in this chapter. This includes the information detailing accumulator replacement, SD card change, software updates, the loading of the accumulator and troubleshooting.

## Accumulator replacement

The accumulator has to be replaced in periodic intervals. The range of an accumulator depends on several factors, including ambient temperature, activity of the Smart Feeder and therefore energy demand of the Smart Feeder. The activity usually depends on the season of the year. As birds have a higher level of activity near the Smart Feeder (SF) during the winter time, the SF is often in the active mode and needs much more energy than during other seasons.

Reasons for accumulator replacement

The accumulators have boards with three LED’s which indicate the state of charge. If three LED’s are blinking this shows that the accumulator is almost empty and should be exchanged as soon as possible. When two LED’s are blinking the accumulator is half full and one LED blinking indicates an almost full accumulator. If there are no LED’s blinking the accumulator is completely empty and no longer able to supply energy.

When all LED’s are lit permanently this indicates a defect at the accumulator or at the accumulator board. In this case the whole accumulator needs to be changed.

Placement of the accumulator

The wind and therefore also rain, snow and mist in Europe primarily come from the west. This can be seen visibly on trees where the western-facing sides are often moss-covered. Therefore, placement of the accumulator on the eastern side can minimize the possibility of damage due to oxidation.

Moreover, the accumulator can be placed in a way that water can drain away at an edge and does not accumulate at the connector or at the cable input.

Operation of the Smart Feeder

19.12.2017 | https://www.orn.mpg.de | Copyright 2017 ©, MPIO Seewiesen | page 50

If the accumulator becomes warm, it can age more rapidly or be damaged. The operating temperature range of the accumulator is between minus 30°C and 55°C according to manufacturer specifications. When the sun shines directly on the accumulator it is possible to exceed this range. Therefore, the accumulator should be protected against direct sunlight through e.g. placement on the north-facing side of a tree or by shading it in another way.

When placing the accumulator, one should be aware of these external environ-mental influences and place the accumulator appropriately, because of the high costs of the accumulators.

## SD card change

The SD cards have a large memory size so that the memory may be filled only after several months or even years.

As continuous recording of data is desired and as unexpected malfunctions of the Smart Feeders are always a possibility, they should be visited and controlled regularly every couple of weeks. In doing so, SD cards can be exchanged and stored data can be checked. If there is unusual data on the SD cards, it could indicate a malfunction of the Smart Feeder. In this case, a maintenance should be arranged.

## Software update

There are three possible methods to write software code on to the flash memory. The debug probe method from IAR systems and the debug interface method without debug probe are always possible. If software has already been written on the flash memory by either of these methods, an additional method using SD cards is also available.

The microcontroller EFM32G230 contains a flash memory with a memory size of 128 KB. This memory contains the software by which the microprocessor works. 128 KB of memory is a sufficient size for operation, even with very complicated applications of the Multifunctional Mainboard to Observe and Manipulate Organisms. Update possibilities are described in more detail in chapter 7.1.

Operation of the Smart Feeder

19.12.2017 | https://www.orn.mpg.de | Copyright 2017 ©, MPIO Seewiesen | page 51

## Loading the accumulator

The accumulators should be changed and charged in regular intervals. The accumulator has to be visually checked for damage when it is changed.

Recharger

Device description | Mascot type 2541 Li, 4 cell, 2A, Lithium Ion Battery Charger, 35W
Manufacturer | Mascot http://www.mascot.no/home/
Nominal power | 35 W
Battery voltage | 12V
Charging current | Up to 2 A
Recommended battery capacity | 1 – 10 Ah
Loadable cells | 4
Charging characteristic | IUoU

The charge process is separated in to three sections.

### 1. Charging current is 2 A until the voltage reaches 14.7 V 2. Voltage will be held at 14.7 V; Current declines slowly 3. A yellow display shows that the charging current is declined under 1 A

4. If the charging current is below 250 mA the recharger switches off.

### 5. In the maintenance charging module the accumulator voltage will be kept at

13.7 V.

Operation of the Smart Feeder

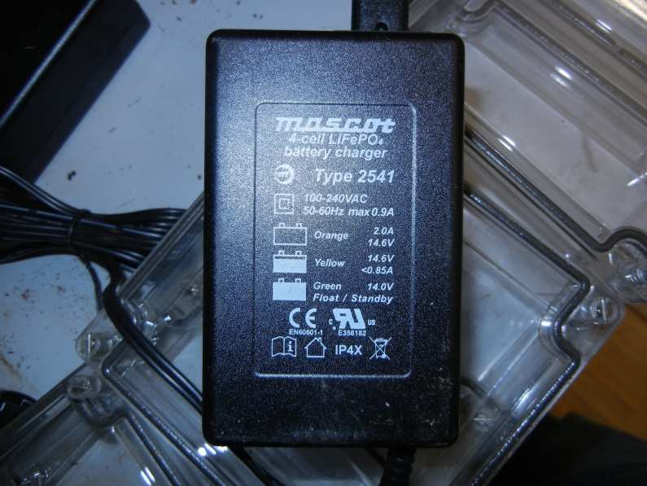
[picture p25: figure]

19.12.2017 | https://www.orn.mpg.de | Copyright 2017 ©, MPIO Seewiesen | page 52

Charging method IUoU

UIoU means that the initial charging current is constant similar to the CCCV charging method until the final charging voltage is reached. Then the voltage is held at the charging end voltage. This constant high voltage can be harmful for the accumulator and reduce the capacity. Therefore, the voltage will be reduced after a certain amount of time; with that the maintenance charging is initiated. With the reduced voltage the accumulator can be charged permanently and the amount of current is roughly like the self-discharge. The “I” in IUoU stands for constant current, “Uo” stands for constant voltage with charging end voltage and “U” for reduced constant Voltage

Operation of the Smart Feeder

19.12.2017 | https://www.orn.mpg.de | Copyright 2017 ©, MPIO Seewiesen | page 53

Charge time

The accumulators can be charged in roughly one day to ensure that the accumulators are securely fully-loaded.

Theoretically, a charging time of roughly 3 hours in both rechargers is enough for a complete loading.

The charging time at the IUoU can be marginally less, because the Uo phase at constant voltage with end-of-charge voltage can be higher than the CV voltage at the CCCV method.

### 7.5 Ah / 2A = 3.75 h

A discharged accumulator with 7.5 Ah requires a charging current of 2A for more than 3.75 hours, because the loading does not take place with a maximal current of 2A the whole time.

## Troubleshooting Smart Feeder

The current version of the Smart Feeder has taken three years of development. Some malfunctions could be encountered and thus lead to experience in troubleshooting and development of specific procedures for malfunctions which may be detected.

Troubleshooting in the field

The field troubleshooting takes place after a malfunction is detected through information from the data collected in the SD cards. Incorrect data indicates a malfunction at the Smart Feeder.

Troubleshooting in the laboratory

Via the LEUART-interface the Smart Feeder can be connected to a PC. This makes it possible to transfer information transmitted by the Microcontroller. This allows for a detailed view into the Smart Feeder.

If the failure cannot be detected via the LEUART-interface, the Smart Feeder has to be measured electronically for further troubleshooting.

Software

19.12.2017 | https://www.orn.mpg.de | Copyright 2017 ©, MPIO Seewiesen | page 54

## Software

The Software on the flash memory in the Multifunctional Mainboard to Observe and Manipulate Organisms is programmed with the programming language C. This software is diverse for different applications and has to be regenerated for every application. It needs to be smaller than 128 KB for the flash memory. The software for the Smart Feeder application will be described in this chapter. It includes reset options, the reset process, how data is stored and what occurs when the SD card is changed. Also described is how regular queries are stored, what can be done with the built-in buttons on the board and the possibility of software updates.

## Reset

The reset can be used to restart the system of the Multifunctional Mainboard to Observe and Manipulate Organisms when an unknown failure occurs. The procedure for a reset is always the same. The reset is a new start and can be compared with the start of a PC.

Possibilities to perform a manual reset

The Multifunctional Mainboard to Observe and Manipulate Organisms can be restarted manually in two ways:

- Via pushbutton
- Reset after electrical energy was not available for considerable time, so

that the capacitor could not provide enough energy. The capacitor has enough energy to provide MOMO for approx. 3 min.

Procedure after reset

After a reset the following procedure takes place:

### 1. Both LED’s (red and orange) will be illuminated to show that the hardware or

software is active and the LED’s are working.

Software

19.12.2017 | https://www.orn.mpg.de | Copyright 2017 ©, MPIO Seewiesen | page 55

Only visible in a terminal program on a PC.

### 2. In case a SD card is recognised, its data system is mounted and the free space

on the memory is displayed. This takes place at every exchange of SD cards during operation.

### 3. Afterwards it will be searched for a log file with the name “BOXnnnn.TXT” (nnnn

is a random decimal number). In the case that the file exists on the SD card the name will be displayed on the LC display otherwise the file “BOX0999.TXT” will be created.

Furthermore, the DCF77 module is switched on to receive date and time. The red LED now flashes to the rhythm of the radio clock signal.

4. After date and time got synchronized, the red LED switched off.

Reset protocol

If a start or a reset of the Multifunctional Mainboard to Observe and Manipulate Organisms is carried out some protocol lines are written on the SD card to com-prehend the process of the maintenance.

20140101-120000.000 DCF77: Enabled

20140101-120000.000 SD-Card Inserted

20140101-120000.054 SD-Card Initialized

20140101-120000.054 SD-Card File System mounted

20140101-120000.497 SD-Card 1938MB free

20140101-120000.499 Using Filename BOX0666.TXT

20140101-120000.517 MCU: EFM32G230F128 HW-ID: 0x245D670356B3C2C0

20140101-120000.550 Battery Manufacturer Name : | Dynamis
20140101-120000.576 Battery Manufacturer Data : | 61.90002/15790
20140101-120000.602 Battery Device Name | : | BMS2-4_V0.3
20140101-120000.629 Battery Device Type | : | Lithium-Ion
20140101-120000.636 Battery Serial Number | : 00008
20140101-120000.643 Battery Design Voltage | : 3.300V per cell

Software

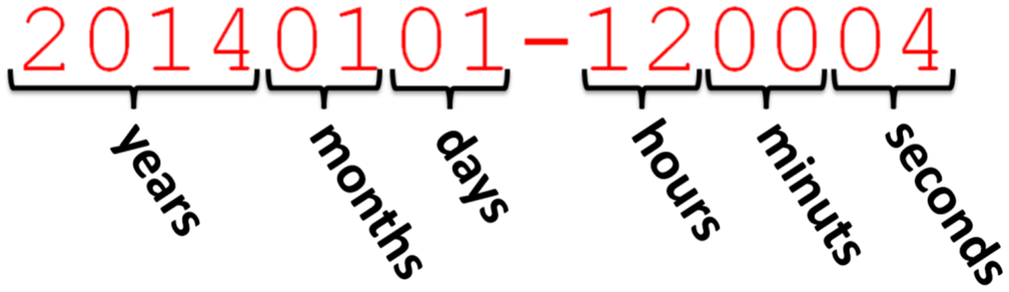
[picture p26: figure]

19.12.2017 | https://www.orn.mpg.de | Copyright 2017 ©, MPIO Seewiesen | page 56
20140101-120000.651 Battery Design Capacity | : 7500mAh

20140101-120000.658 Battery Full Charge Capac.: 8079mAh

20140101-120000.666 Battery Remaining Capacity: 7268mAh

20140101-120000.674 Battery Runtime to empty | : More than 6 weeks
20140101-120000.681 Battery Actual Voltage | : 13.3V
20140101-120000.689 Battery Actual Current | : | 0mA

20140101-120000.690 Reading Configuration File CONFIG.TXT

## Data storage

All important information from the RAM memory will be saved in a txt-file on the SD card. Every event or stored message begins with the date and time of the event.

Following the date and time there is a blank space. Then follows the actual status message.

Procedure after SD card change

After a new SD card is plugged in the following procedure starts.

1. It displays that a new SD card has been detected.

20140101-120004 SD-Card Inserted

20140101-120004 SD-Card Initialized

20140101-120004 SD-Card File System mounted

Software

19.12.2017 | https://www.orn.mpg.de | Copyright 2017 ©, MPIO Seewiesen | page 57
2. The following line shows how much free space remains on the SD card.

20140101-120011 SD-Card 1880MB free

### 3. Afterwards it will search for a log file with the name „BOXnnnn.TXT“ (nnnn is a

random decimal number). In case that the file exists on the SD card the name will be displayed on the LC display otherwise the file „BOX0999.TXT“ will be created.

20140101-120011 Using Filename BOX0999.TXT

20140101-120011 Media Change: BOX0999.TXT -> BOX0020.TXT

### 4. The hardware ID will be displayed, which is a unique number allocated to each

Multifunctional Mainboard to Observe and Manipulate Organisms

20140101-120011 MCU: EFM32G230F128 HW-ID: 0x24B4010253FD82EE

### 5. The status of the accumulator is then displayed, including the manufacturer

name, manufacturer data, device name, device type, serial number, design voltage, design capacity, total capacity, remaining capacity, remaining time at actual current and at least the measured actual voltage.

20140101-120011 Battery Manufacturer Name : | Dynamis
20140101-120011 Battery Manufacturer Data : | 61.90002/15790
20140101-120011 Battery Device Name | : | BMS2-4_V0.3
20140101-120011 Battery Device Type | : | Lithium-Ion
20140101-120011 Battery Serial Number | : 00008
20140101-120011 Battery Design Voltage | : 3.300V per cell
20140101-120012 Battery Design Capacity | : 7500mAh

20140101-120012 Battery Full Charge Capac.: 8968mAh

20140101-120012 Battery Remaining Capacity: 4122mAh

20140101-120012 Battery Runtime to empty | : More than 6 weeks
20140101-120012 Battery Actual Voltage | : 13.149V
20140101-120012 Battery Actual Current | : | 3mA

Software

19.12.2017 | https://www.orn.mpg.de | Copyright 2017 ©, MPIO Seewiesen | page 58

### 6. The configuration file CONFIG.txt is read. This process enables the

manipulation of the different identities. Up to 52 identities can be programed. A detailed description can be found in the CONFIG.txt file. Attention should be paid to further settings of energy-saving times, light barrier logic for known birds, animal transponder readers, switching off time and transponder identification for unknown identities (UNKNOWN). Standard stocks for flaps and cameras.

20140101-120000.690 Reading Configuration File CONFIG.TXT

ON_TIME | : 03:35
OFF_TIME | : 22:40
LB_FILTER_DURATION | : 10

RFID_PWR_OFF_TIMEOUT : 360

RFID_DETECT_TIMEOUT | : 15
KEEP_OPEN | : 60
KEEP_CLOSED | : 120
CAM1_DURATION | : 15

: KEEP_OPEN : KEEP_CLOSED : CAM1_DURATION

108196A801AF0001 | : | 180 | : | default | : | default
9E1CE7D001AF0001 | : | ALWAYS | : | default | : | default
ANY | : | 120 | : | 240 | : | 360
D5CD24B43A6F0001 | : | ALWAYS | : | default | : | default

### 7. The time of the microcontroller is updated through the signals from the radio

clock. This process usually only takes a few minutes.

20140101-120856 DCF77: Time Frame 1 is 20160315-143100

20140101-120956 DCF77: Time Frame 2 is 20160315-143200

20160315-143200 Initial Time Synchronisation

20160315-143200 DCF77: Time Synchronization 14:32:00

20160315-143200 DCF77: Disabled

Software

19.12.2017 | https://www.orn.mpg.de | Copyright 2017 ©, MPIO Seewiesen | page 59

## Periodic routine queries

Time update

Every 24 hours, during the night the time from the microcontroller is updated by the signals from the radio clock.

20170304-015500.000 DCF77: Enabled

20170304-015659.279 DCF77: Time Frame 1 is 20170304-015700

20170304-015759.283 DCF77: Time Frame 2 is 20170304-015800

20170304-015800.284 DCF77: Time Synchronization 01:58:00 (MEZ)

20170304-015800.001 DCF77: Disabled

Further outputs:

Log ("DCF77: Changing time zone from MEZ to MESZ");

Log ("DCF77: Changing time zone from MESZ to MEZ”);

If the DCF77 is not connected, there is no sync signal and no synchronisation.

Battery status query

At 11 a.m. and 11 p.m. the battery status is written on the memory as well as on the SD card. In addition, the current power demand is calculated. The range of the accumulator is calculated from data taken from the accumulator board. The remaining capacity and the current power demand are used for the calculation of the remaining range.

20170303-230000.014 Battery Remaining Capacity: 7271mAh

20170303-230000.021 Battery Runtime to empty | : More than 6 weeks
20170303-230000.029 Battery Actual Voltage | : 13.3V
20170303-230000.036 Battery Actual Current | : | 0mA

Software

19.12.2017 | https://www.orn.mpg.de | Copyright 2017 ©, MPIO Seewiesen | page 60

## Recorded events

One task of the Multifunctional Mainboard to Observe and Manipulate Organisms is to record the behaviour of animals. In the Smart Feeder application this is achieved via recordings from the light barrier activity and transponder detections as well as via the closing of the shutter.

Light barrier activity

The light barriers are always active and are always supplied with electrical energy. They are the trigger for the RFID Reader which is by far the largest energy consumer.

20160323-112408 LBO:ON | # Light barrier outer on
20160323-112408 LBI:ON | # Light barrier inner on
20160323-112408 LBO:off | # Light barrier outer off
20160323-112408 LBI:off | # Light barrier inner off

Transponder activity

The RFID reader is switched on by light barrier activity. This needs to occur very quickly as the transponder may be rapidly moving through the barrier and its number needs to be read completely. The birds have a particularly high velocity when approaching, which is why the RFID Reader needs to be activated very quickly.

20150723-154010 RFID is powered ON

20150723-154010 Transponder: D5CD24B43A6F0001

20150723-154122 RFID is powered off

Because it is likely to detect further activity after a transponder is detected, the RFID remains on for an additional 6 minutes after the last transponder signal.

Software

19.12.2017 | https://www.orn.mpg.de | Copyright 2017 ©, MPIO Seewiesen | page 61

Servomotor activity

The servomotor is closed or opened after the query of the CONFIG.txt file. .

20170317-114613.295 Shutter will be opened

20170317-114528.437 Shutter will be closed

Connections for possible recording devices (camera)

20170317-105658.000 CAM1 is powered on

20170317-105758.000 CAM1 is powered off

20170317-105658.000 CAM2 is powered on

20170317-105758.000 CAM2 is powered off

Standard recording

In the following there are typical status messages:

20170317-112428.223 LB1:ON

20170317-112428.223 CAM1 is powered ON

20170317-112428.224 RFID is powered ON

20170317-112428.584 Transponder: 0B6122B43A6F0001:0:A:15

20170317-112428.585 Shutter will be closed

20170317-112428.823 LB1:off

20170317-112428.823 LB1:off

20170317-112452.000 CAM1 is powered off

20170317-113038.000 RFID is powered off

Software

19.12.2017 | https://www.orn.mpg.de | Copyright 2017 ©, MPIO Seewiesen | page 62

Power Good and Power Fail

- Battery gets disconnected
- Power fail gets detected
- RFID Reader and CAM1 get switched off
- Battery gets reconnected
- normal function without reset, RFID Reader and CAM1 get reactivated on demand

4/18/2017 12:45:06.274 [RX] - 20170418-124506.221 Power-Fail: Received interrupt (POWER FAIL)

4/18/2017 12:51:44.342 [RX] - 20170418-125144.296 LB1:ON

20170418-125144.402 LB2:ON

4/18/2017 12:51:45.030 [RX] - 20170418-125144.985 LB1:off

20170418-125144.986 LB2:off

4/18/2017 12:53:59.514 [RX] - 20170418-125359.436 Power-Fail: Received interrupt (POWER GOOD)

Software

19.12.2017 | https://www.orn.mpg.de | Copyright 2017 ©, MPIO Seewiesen | page 63

## Occurrences when it is not possible to write on the SD card

When the SD card is full or if there is no SD card is in SD card slot an error message is written on the LEUART-BUS. During a normal operation of the Smart Feeder application of the Multifunctional Mainboard to Observe and Manipulate Organisms, it is not common that data is lost due to an absent or malfunctioning SD card, because the internal memory for events provides 2 KB, which should be sufficient for many events to be stored.

ERROR: Log Buffer Out of Memory - lost 1 Messages (only appears on
HyperTerminal screen of the PC)

More error messages:

ERROR Config File - Line 131, pos 26, ID: OUT OF MEMORY

SMB_Reset: Try to recover from invalid state

SMB_Reset: Recovery failed, giving up

CfgRead: FILE OPEN - Error Code

CfgRead: FILE READ - Error Code

CfgRead: Line %d too long

Config File - Line %d, pos %ld: Invalid Variable Name

Config File - Line %d, pos %ld: Unknown Variable

Config File - Line %d, pos %ld: Unknown Variable

Config File - Line %d, pos %ld: Value expected

Config File - Line %d, pos %ld, %s: Invalid time

Config File - Line %d, pos %ld, %s: OUT OF MEMORY

Config File - Line %d, pos %ld, %s: Unsupported data type

Config File - Line %d, pos %ld: Garbage at end of line

LogError ("LogFileOpen: Error Code %d", res);

See if Log File is open */

LogError ("LogFlush: Init Failed");

LogError ("LogFlush: Error Code %d", res);

LogError ("LogFlush: Disk Full");

Expiry after keystroke

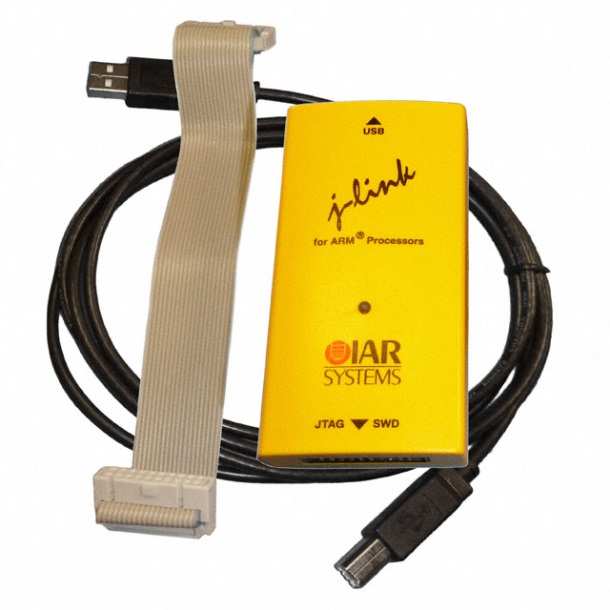
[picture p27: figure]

19.12.2017 | https://www.orn.mpg.de | Copyright 2017 ©, MPIO Seewiesen | page 64

## Expiry after keystroke

The Multifunctional Mainboard to Observe and Manipulate Organisms contains a button for conducting a reset.

After pressing the S1 button, the whole system will be restarted. The procedure of the restart is described in chapter Fehler! Verweisquelle konnte nicht gefunden werden..

## Update options

There are three possibilities to write software code on the flash memory.
The method of the Debug Probe and the one via the Debug Interface always work. If software was written on the flash memory via either one of these the methods examining the content of a newly inserted SD card and searching for software updates, a third method can be implemented.

## IAR Systems Debug Probe

Through the debug probe from IAR systems it is possible to load compiled software code on the flash memory. The software from IAR for the debug probe is necessary for this.

IAR Systems also distribute the software IAR Embedded Workbench to create and compile C code. The compiled C code can be loaded on the flash memory by the debug probe.

Expiry after keystroke

19.12.2017 | https://www.orn.mpg.de | Copyright 2017 ©, MPIO Seewiesen | page 65

## With USB on 10-pole Debug Interface Connector

This method only allows HEX and BIN files to be transferred to the flash memory and has the benefit of the original C code not being readable anymore.

## Via SD card and boot loader

If software has already been written on the flash memory by either of the methods from chapter 7.2 or 7.3 a third method through a boot loader is available. If the software of the flash memory contains the command to search for new software when recognizing a new SD card, this new software can be installed.

Contact details

19.12.2017 | https://www.orn.mpg.de | Copyright 2017 ©, MPIO Seewiesen | page 66

## Contact details

address | Max-Planck-Institut für Ornithologie Eberhard-Gwinner-Str. 82319 Seewiesen
web address | http://www.orn.mpg.de/
electronics developer | Dipl. Ing. (FH) Peter Loës
e-mail address | loes@orn.mpg.de
telephone number | Tel: +49 8157 932-330

Links to the datasheets

19.12.2017 | https://www.orn.mpg.de | Copyright 2017 ©, MPIO Seewiesen | page 67

## 8. Links to the datasheets

Datasheets need to be saved within the folder ‘datasheets’, which has to be in the same content as the documentation. For every link there is a document within this folder.

EFM32G230

IAR J Tag ARM

LC display

SD card reader

Button

Capacitor

Jack connector

USB cable

Down converter

LED’S

Radio clock

Light barrier

RFID reader

RFID transponder

Housing for the main board

Housing for the accumulator

Battery charger Fronius

Battery charger Mascot

Battery cell

Content

19.12.2017 | https://www.orn.mpg.de | Copyright 2017 ©, MPIO Seewiesen | page 68

## Content

List of abbreviations | 3
System Overview | 4
General Description of Functions | 4
System configuration main circuit board | 7
Hardware Illustration (MOMO) | 7
Buttons | 9
Connections for linear actuator control | 9
Connections for two passive infrared detectors | 10
Connections for limit switch | 10
Power supply for servomotor | 11

Connections for switchable power supplies for three RFID reading
devices | 11
Power supply for MOMO | 13
Debug Interface (DBG) | 13
EFM32 Microcontroller | 14
Capacitor | 15
Connecting terminal for the radio clock | 16
Output voltages (down converter) | 16
Power supply for light barrier | 17
SMBus „System Management Bus“ | 17
Jack connector as interface to a PC | 18
LEDs | 18

Content

19.12.2017 | https://www.orn.mpg.de | Copyright 2017 ©, MPIO Seewiesen | page 69
SD Memory Card Connector | 18
System configuration radio clock receiver | 19
Connector | 19
Hardware illustration | 19
Radio clock | 20
Smart Feeder (Hardware) | 21
Hardware illustration Smart Feeder | 21
Light barriers | 23
RFID Reader for transponders | 24
Servomotor | 27
Dashcam | 28
Accumulator | 29
Pin assignment and connectors | 30
Pin allocation | 30

Technical description of additional connectivity options for applications 35

Housing | 39
Housing for the main board | 39
Housing for the accumulator | 40
General working conditions | 41
Energy supply | 42
Current supply | 43
ARM Cortex Processor | 43

Content

19.12.2017 | https://www.orn.mpg.de | Copyright 2017 ©, MPIO Seewiesen | page 70
RFID | 43
Light barriers | 43
Radio clock | 43
LED | 43
Accumulator LED’s and self-discharge | 44
Overview of the nominal currents | 44
Overview of the currents in the different operating modes | 45
Voltage supply | 47
Electrical energy storage | 47
Accumulator | 47
Capacitor | 47
Conversion losses | 48
Range estimation of the accumulator | 48
Operation of the Smart Feeder | 49
Accumulator replacement | 49
Reasons for accumulator replacement | 49
Placement of the accumulator | 49
SD card change | 50
Software update | 50
Loading the accumulator | 51
Recharger | 51
Charging method IUoU | 52

Content

19.12.2017 | https://www.orn.mpg.de | Copyright 2017 ©, MPIO Seewiesen | page 71
Charge time | 53
Troubleshooting Smart Feeder | 53
Troubleshooting in the field | 53
Troubleshooting in the laboratory | 53
Software | 54
Reset | 54
Possibilities to perform a manual reset | 54
Procedure after reset | 54
Reset protocol | 55
Data storage | 56
Periodic routine queries | 59
Time update | 59
Battery status query | 59
Recorded events | 60
Light barrier activity | 60
Transponder activity | 60
Servomotor activity | 61
Connections for possible recording devices (camera) | 61
Standard recording | 61
Power Good and Power Fail | 62
Occurrences when it is not possible to write on the SD card | 63
Procedure after button usage | 64

Content

19.12.2017 | https://www.orn.mpg.de | Copyright 2017 ©, MPIO Seewiesen | page 72
Update options | 64
IAR Systems Debug Probe | 64
With USB on 10-pole Debug Interface Connector | 65
Via SD card and boot loader | 65
Contact details | 66

### 8. Links to the datasheets | 67

Content | 68

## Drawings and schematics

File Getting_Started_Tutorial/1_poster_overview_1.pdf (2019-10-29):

## Multifunctional Mainboard to Observe and Manipulate Organisms (MOMO) RFID Readers and SERVO Engines

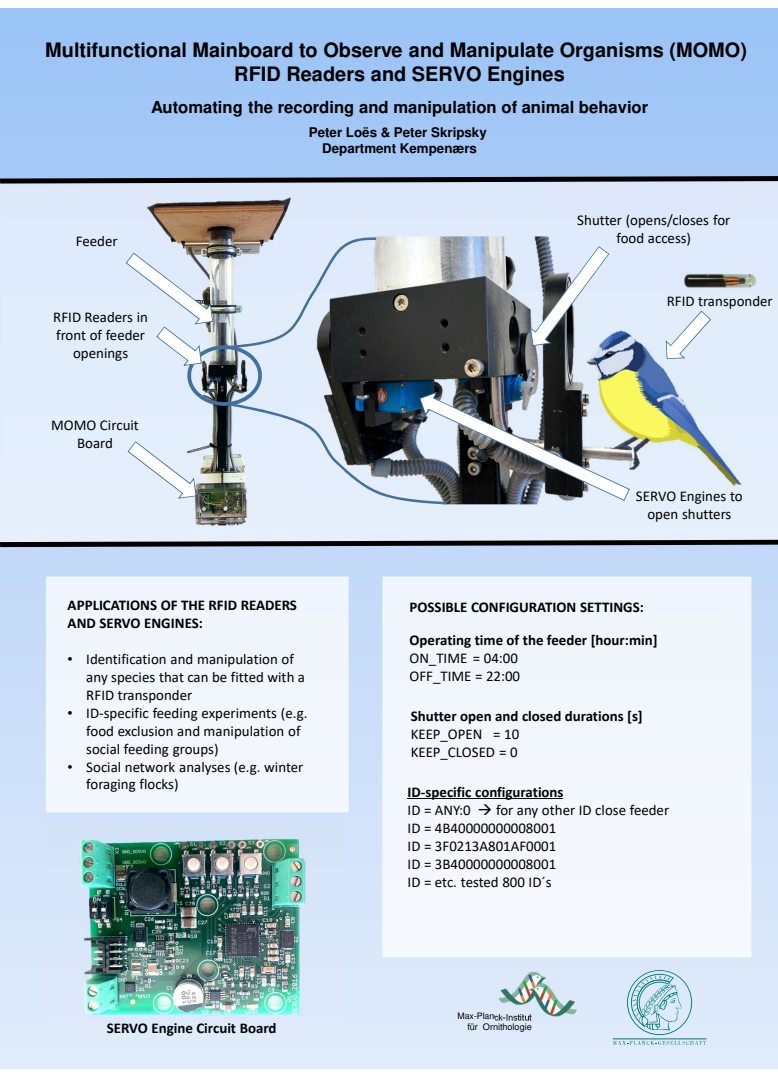
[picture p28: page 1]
APPLICATIONS OF THE RFID READERS; POSSIBLE CONFIGURATION SETTINGS:; Feeder; RFID transponder; MOMO Circuit Board

Automating the recording and manipulation of animal behavior

Peter Loës & Peter Skripsky
Department Kempenærs

Shutter (opens/closes for
food access)

RFID Readers in
front of feeder
openings

SERVO Engines to
open shutters

AND SERVO ENGINES:

Operating time of the feeder [hour:min]
ON_TIME = 04:00
OFF_TIME = 22:00

• Identification and manipulation of
any species that can be fitted with a
RFID transponder
• ID-specific feeding experiments (e.g.
food exclusion and manipulation of
social feeding groups)
• Social network analyses (e.g. winter
foraging flocks)

Shutter open and closed durations [s]
KEEP_OPEN = 10
KEEP_CLOSED = 0

ID-specific configurations
ID = ANY:0 → for any other ID close feeder
ID = etc. tested 800 ID´s

Max-Planck-Institut
für Ornithologie

SERVO Engine Circuit Board

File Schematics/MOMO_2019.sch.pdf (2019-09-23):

# Power Input

# EFM32 Power Regulator

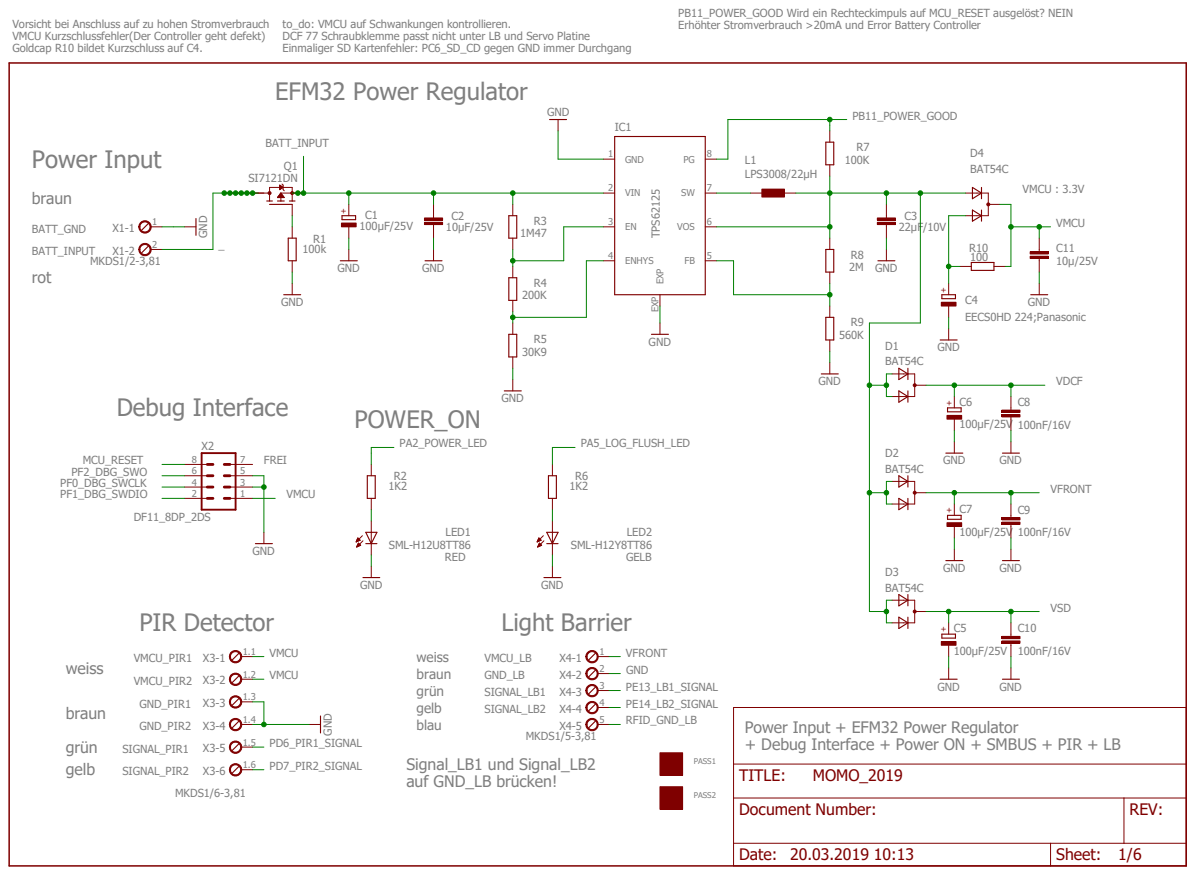
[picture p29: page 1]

PB11_POWER_GOOD Wird ein Rechteckimpuls auf MCU_RESET ausgelöst? NEIN
Erhöhter Stromverbrauch >20mA und Error Battery Controller

Vorsicht bei Anschluss auf zu hohen Stromverbrauch
VMCU Kurzschlussfehler(Der Controller geht defekt)
Goldcap R10 bildet Kurzschluss auf C4.

to_do: VMCU auf Schwankungen kontrollieren.
DCF 77 Schraubklemme passt nicht unter LB und Servo Platine
Einmaliger SD Kartenfehler: PC6_SD_CD gegen GND immer Durchgang

Power Input + EFM32 Power Regulator
+ Debug Interface + Power ON + SMBUS + PIR + LB

Document Number: | REV:

Date: 20.03.2019 10:13 | Sheet: 1/6

# EFM32 I/O + POWER

## CL f. 32KHz crystal = 22pF as in STK3600

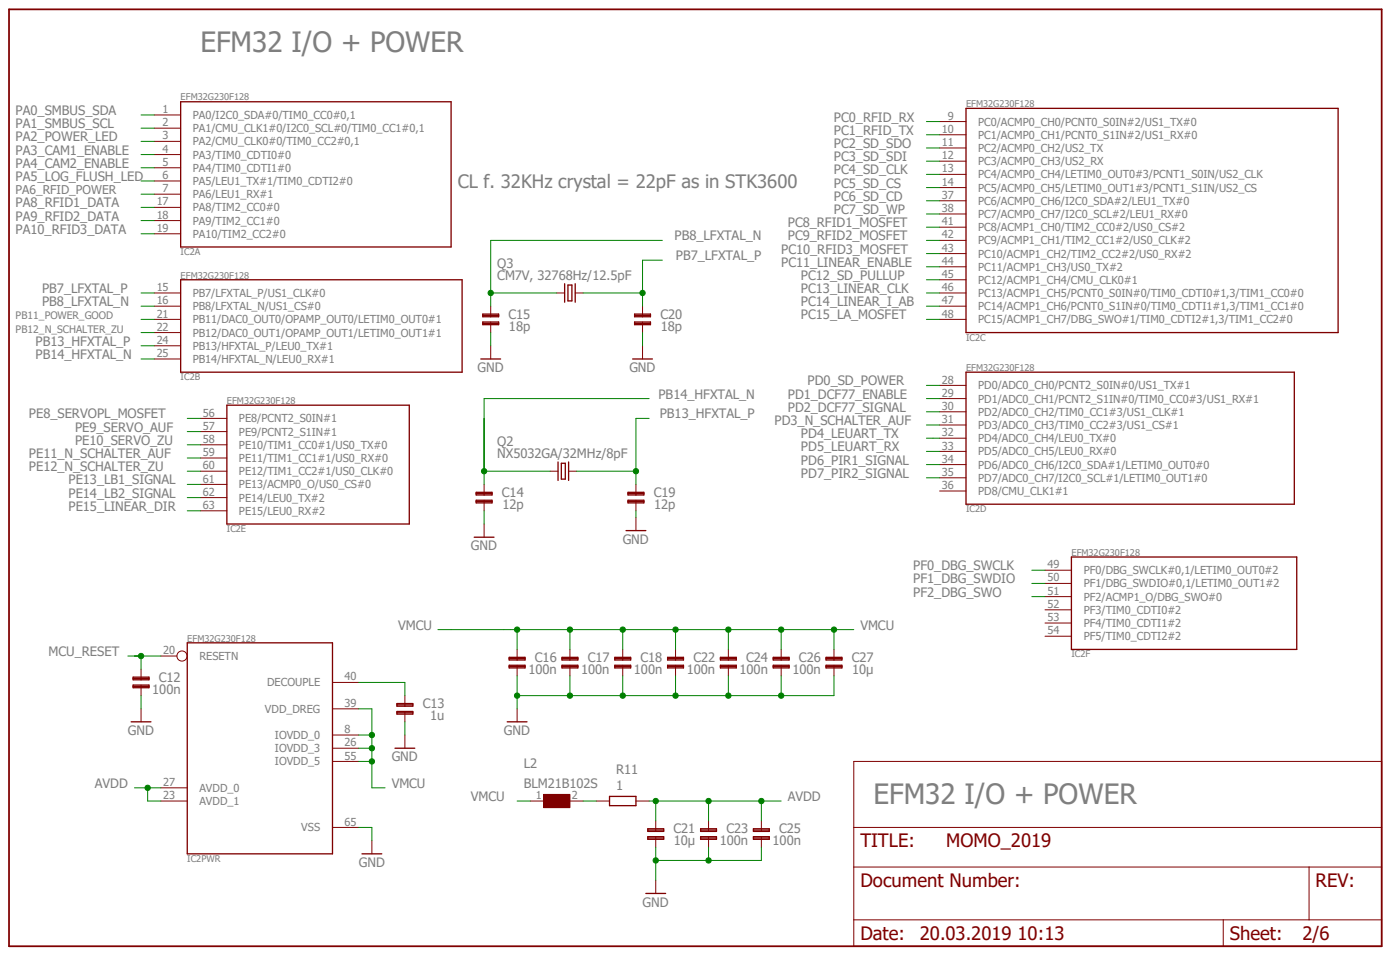
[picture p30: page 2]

Document Number: | REV:

Date: 20.03.2019 10:13 | Sheet: 2/6

## Activity

# SD SOCKET + DCF77 + LEUART

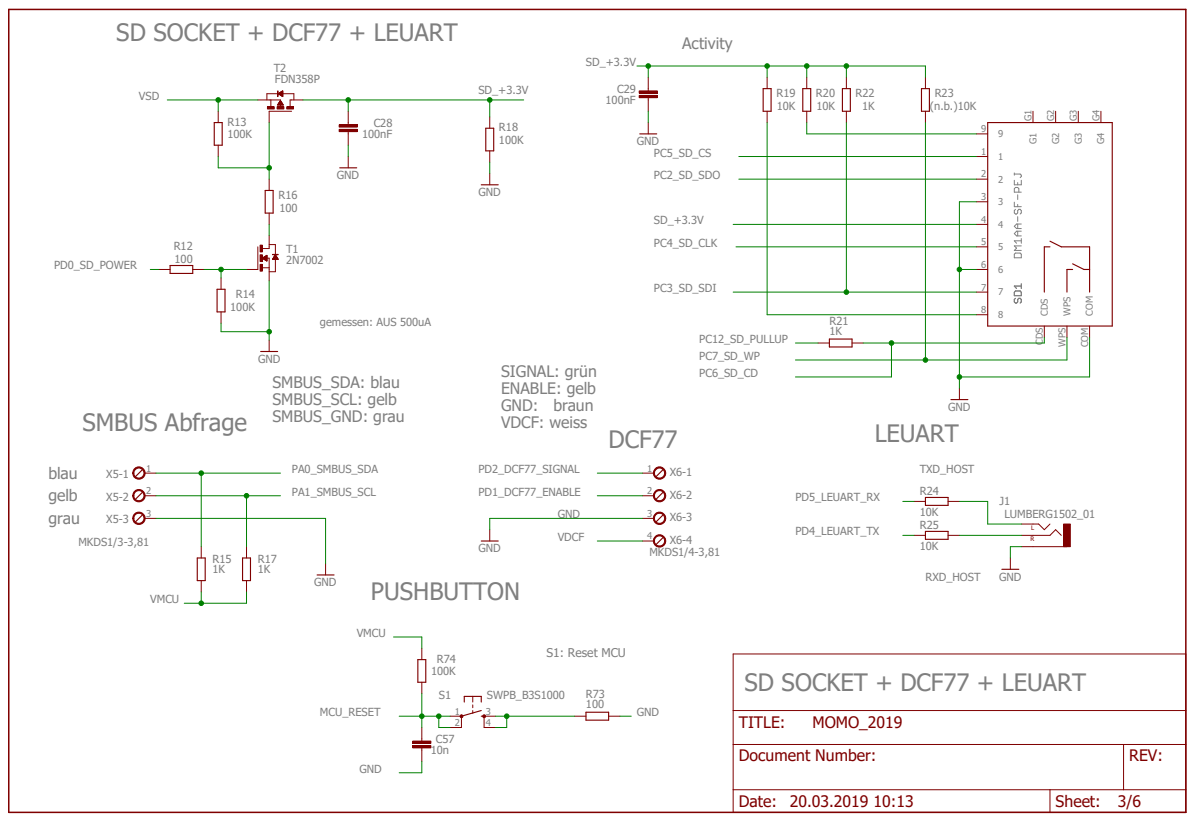
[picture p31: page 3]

Document Number: | REV:

Date: 20.03.2019 10:13 | Sheet: 3/6

# RFID_Trigger

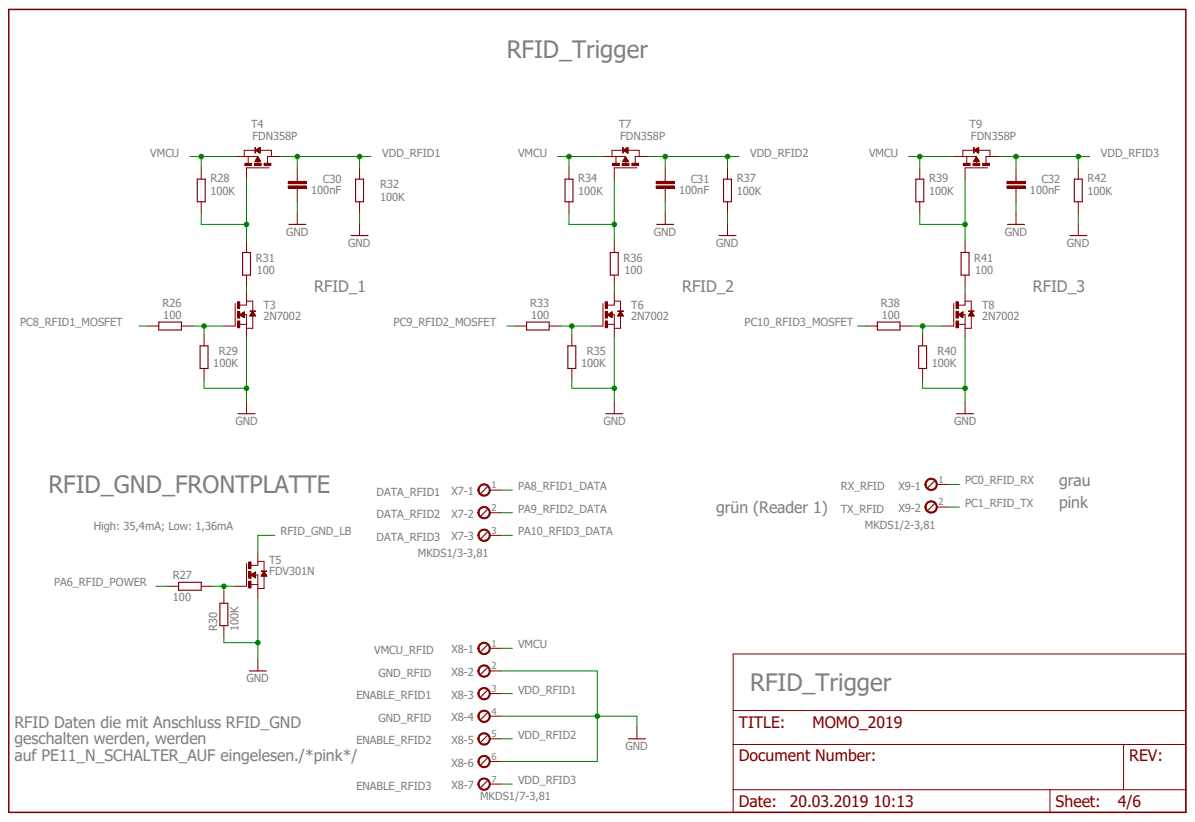
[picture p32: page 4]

RFID Daten die mit Anschluss RFID_GND
geschalten werden, werden
auf PE11_N_SCHALTER_AUF eingelesen./*pink*/

Document Number: | REV:

Date: 20.03.2019 10:13 | Sheet: 4/6

## 5V_Ausgabe

# POWER OUTPUTs

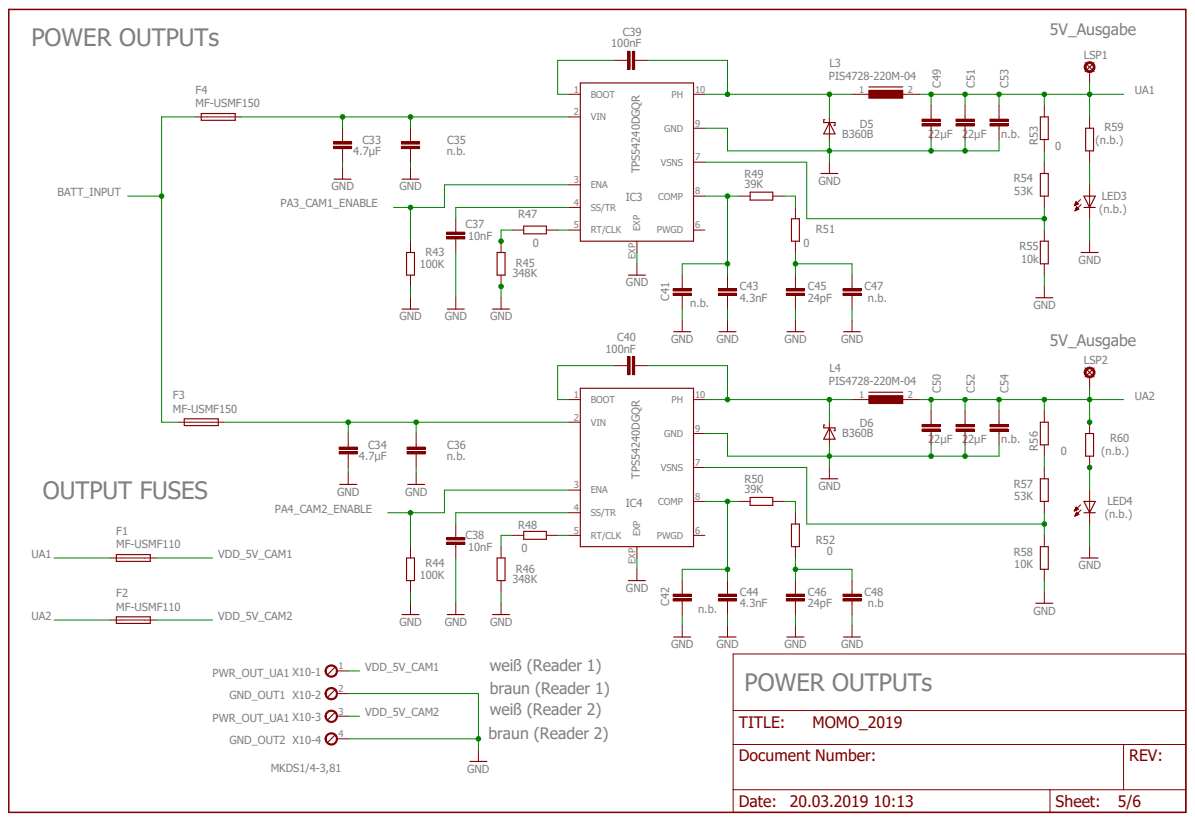
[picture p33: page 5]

Document Number: | REV:

Date: 20.03.2019 10:13 | Sheet: 5/6

# SERVOANSTEUERUNG FUSES

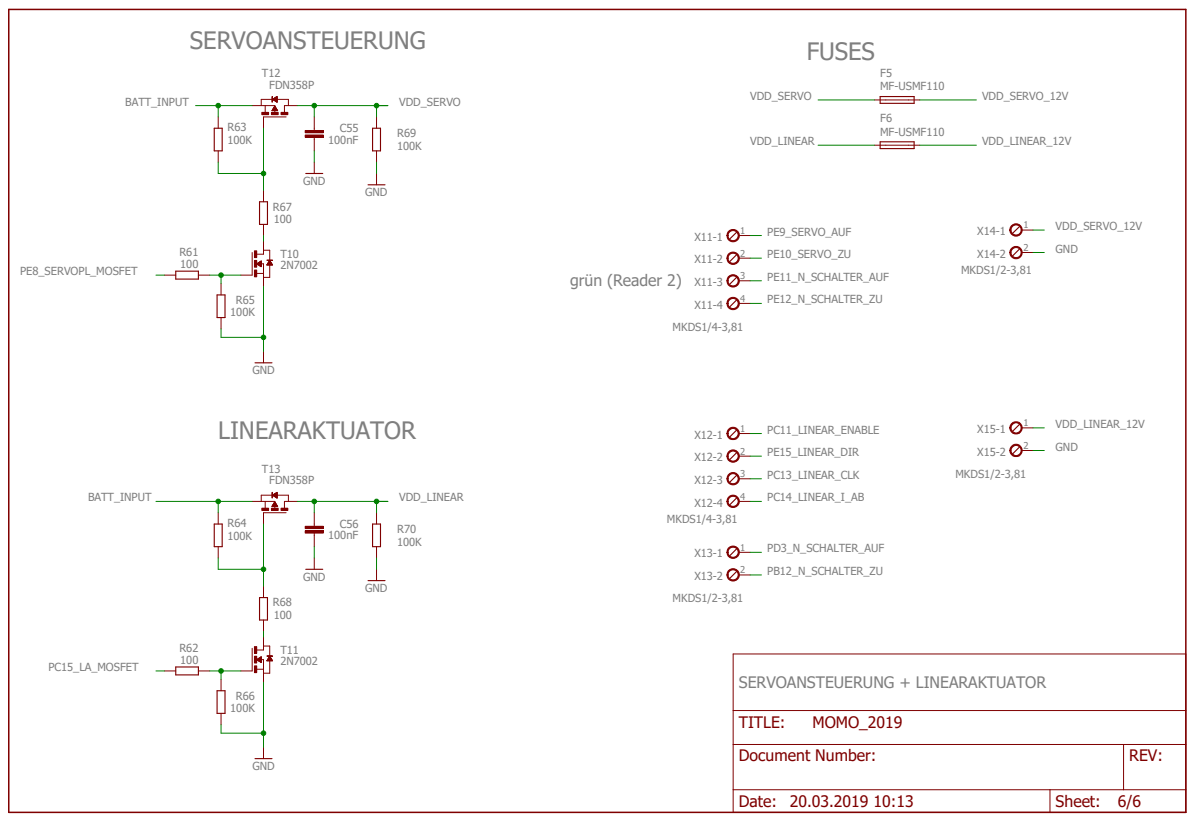
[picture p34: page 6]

Document Number: | REV:

Date: 20.03.2019 10:13 | Sheet: 6/6

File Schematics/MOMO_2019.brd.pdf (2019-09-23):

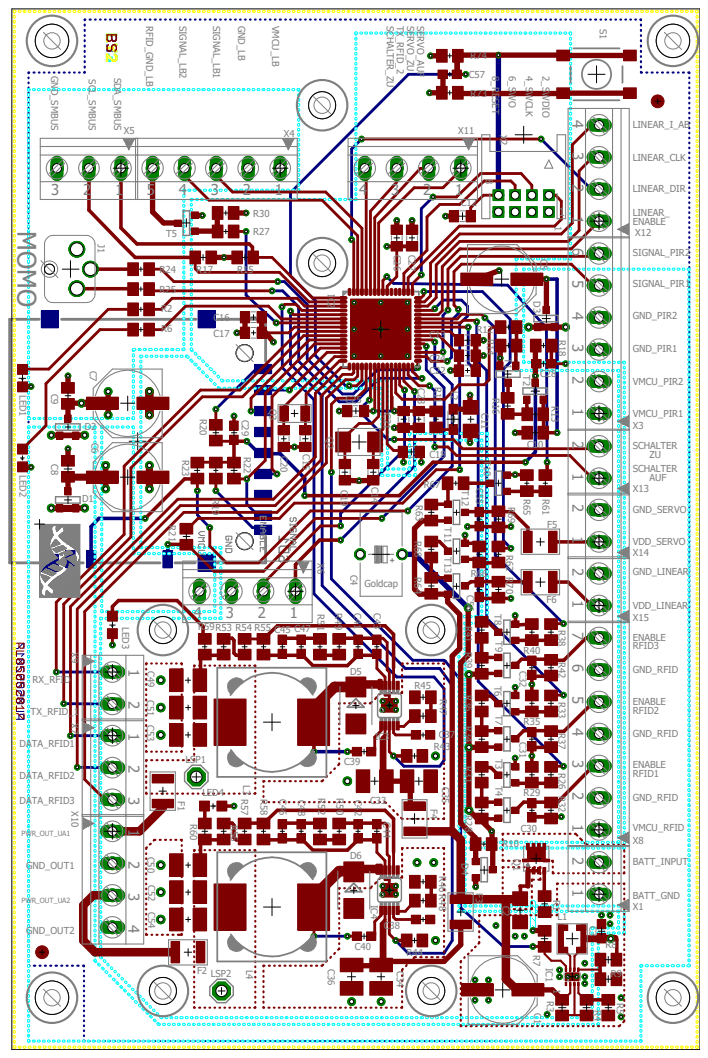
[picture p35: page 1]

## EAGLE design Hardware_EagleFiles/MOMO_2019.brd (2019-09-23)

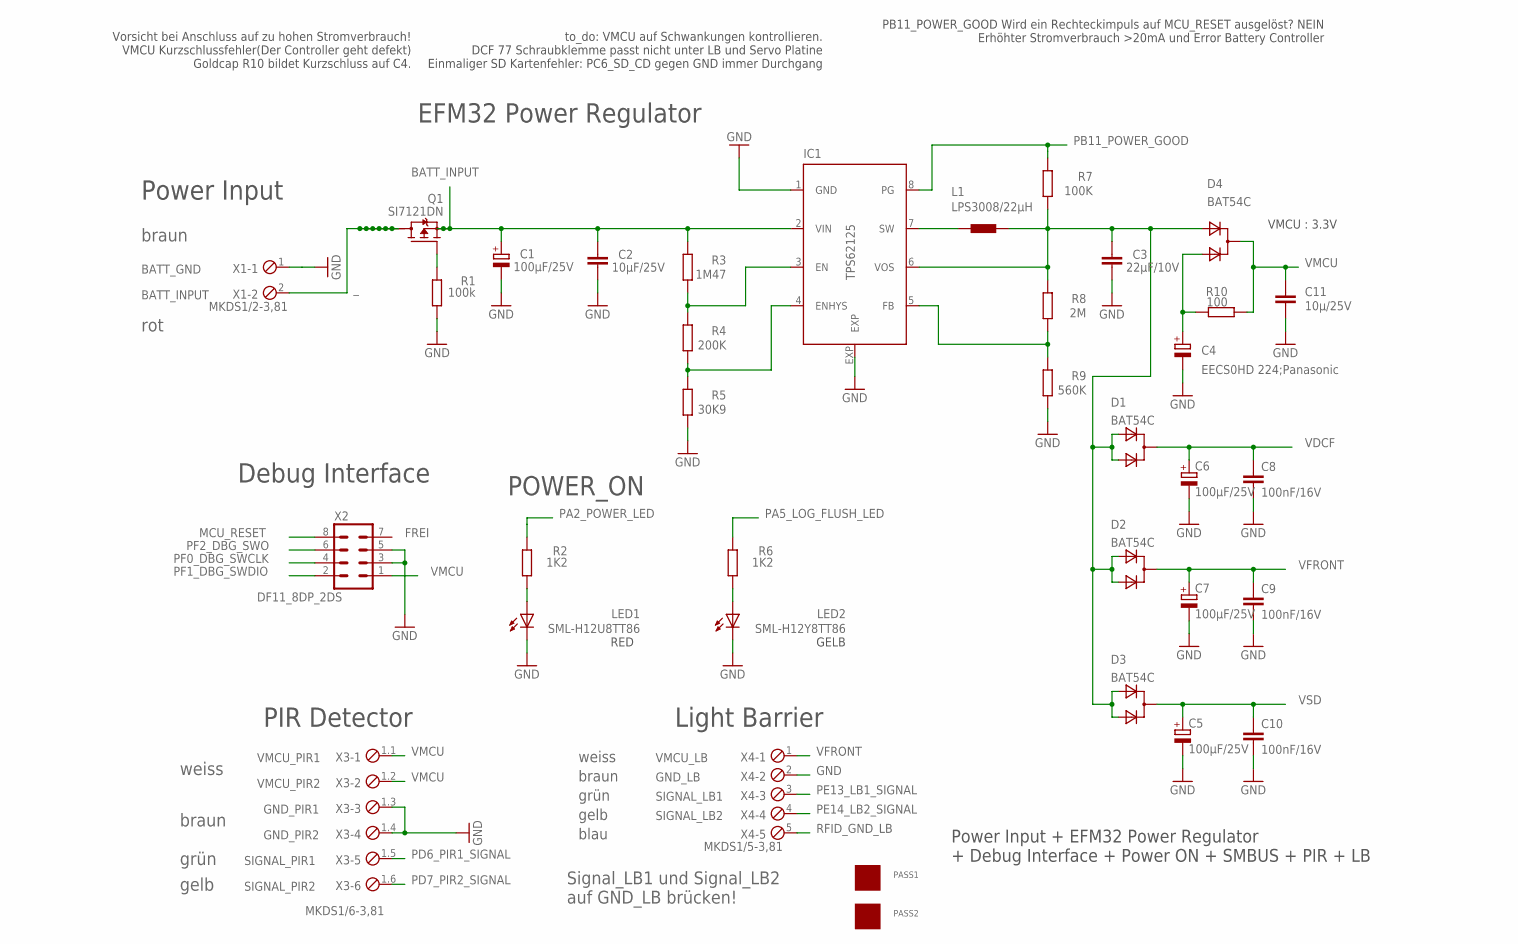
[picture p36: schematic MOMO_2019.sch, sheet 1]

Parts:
C1, C5, C6, C7: 100µF/25V; PANASONIC_E
C2: 10µF/25V; C1206
C3: 22µF/10V; C0603
C4: EECS0HD 224;Panasonic; GOLDCAPSPK-V
C8, C9, C10: 100nF/16V; C0805
C11: 10µ/25V; C1206
D1, D2, D3, D4: BAT54C; SOT-23$1
IC1: TPS62125; DSG_PWSO-N8_EXP
L1: LPS3008/22µH; LPS3008
LED1: SML-H12U8TT86; CHIPLED_0805
LED2: SML-H12Y8TT86; CHIPLED_0805
PASS1, PASS2: ROUND_1MM1.5; ROUND2_1.5MM
Q1: SI7121DN; TRANSISTOR-FET_1212-8S
R1: 100k; R0805
R2, R6: 1K2; R0805
R3: 1M47; R0805
R4: 200K; R0805
R5: 30K9; R0805
R7: 100K; R0805
R8: 2M; R0805
R9: 560K; R0805
R10: 100; R0805
X1: MKDS1/2-3,81; 2POL381
X2: DF11_8DP_2DS; DP11_8DP-2DS
X3: MKDS1/6-3,81; 6POL381
X4: MKDS1/5-3,81; 5POL381

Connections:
1: C3.1, D1.2 (A1), D1.3 (A2), D2.2 (A1), D2.3 (A2), D3.2 (A1), D3.3 (A2), D4.2 (A1), IC1.6 (VOS), L1.2, R7.1, R8.2
BATT_INPUT: C1.+, C2.1, IC1.2 (VIN), Q1.1 (S), Q1.2 (S), Q1.3 (S), R3.2; also elsewhere on the board
GND: C1.-, C2.2, C3.2, C4.-, C5.-, C6.-, C7.-, C8.2, C9.2, C10.2, C11.1, IC1.1 (GND), IC1.EXP, LED1.C, LED2.C, R1.1, R5.1, R9.1, X1.1, X2.3, X2.5, X3.1.3, X3.1.4, X4.2; also elsewhere on the board
MCU_RESET: X2.8; also elsewhere on the board
unnamed: LED2.A, R6.2
unnamed: C4.+, D4.3 (A2), R10.2
unnamed: IC1.3 (EN), R3.1, R4.2
unnamed: IC1.4 (ENHYS), R4.1, R5.2
unnamed: IC1.7 (SW), L1.1
unnamed: Q1.4 (G), R1.2
unnamed: LED1.A, R2.2
unnamed: IC1.5 (FB), R8.1, R9.2
PA2_POWER_LED: R2.1; also elsewhere on the board
PA5_LOG_FLUSH_LED: R6.1; also elsewhere on the board
PB11_POWER_GOOD: IC1.8 (PG), R7.2; also elsewhere on the board
PD6_PIR1_SIGNAL: X3.1.5; also elsewhere on the board
PD7_PIR2_SIGNAL: X3.1.6; also elsewhere on the board
PE13_LB1_SIGNAL: X4.3; also elsewhere on the board
PE14_LB2_SIGNAL: X4.4; also elsewhere on the board
PF0_DBG_SWCLK: X2.4; also elsewhere on the board
PF1_DBG_SWDIO: X2.2; also elsewhere on the board
PF2_DBG_SWO: X2.6; also elsewhere on the board
RFID_GND_LB: X4.5; also elsewhere on the board
VDCF: C6.+, C8.1, D1.1 (C); also elsewhere on the board
VFRONT: C7.+, C9.1, D2.1 (C), X4.1
VMCU: C11.2, D4.1 (C), R10.1, X2.1, X3.1.1, X3.1.2; also elsewhere on the board
VSD: C5.+, C10.1, D3.1 (C); also elsewhere on the board
_: Q1.5 (D), Q1.6 (D), Q1.7 (D), Q1.8 (D), Q1.9 (D), Q1.10 (D), Q1.11 (D), X1.2

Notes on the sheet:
BATT_GND
BATT_INPUT
Power Input + EFM32 Power Regulator + Debug Interface + Power ON + SMBUS + PIR + LB
Power Input
EFM32 Power Regulator
Debug Interface
POWER_ON
FREI
SIGNAL_PIR1
VMCU_PIR1
VMCU_PIR2
GND_PIR1
GND_PIR2
SIGNAL_PIR2
VMCU : 3.3V
weiss
braun
grün
gelb
VMCU_LB
GND_LB
SIGNAL_LB1
SIGNAL_LB2
PIR Detector
Light Barrier
RED
GELB
blau
rot
to_do: VMCU auf Schwankungen kontrollieren. DCF 77 Schraubklemme passt nicht unter LB und Servo Platine Einmaliger SD Kartenfehler: PC6_SD_CD gegen GND immer Durchgang
Vorsicht bei Anschluss auf zu hohen Stromverbrauch! VMCU Kurzschlussfehler(Der Controller geht defekt) Goldcap R10 bildet Kurzschluss auf C4.
PB11_POWER_GOOD Wird ein Rechteckimpuls auf MCU_RESET ausgelöst? NEIN Erhöhter Stromverbrauch >20mA und Error Battery Controller
Signal_LB1 und Signal_LB2 auf GND_LB brücken!

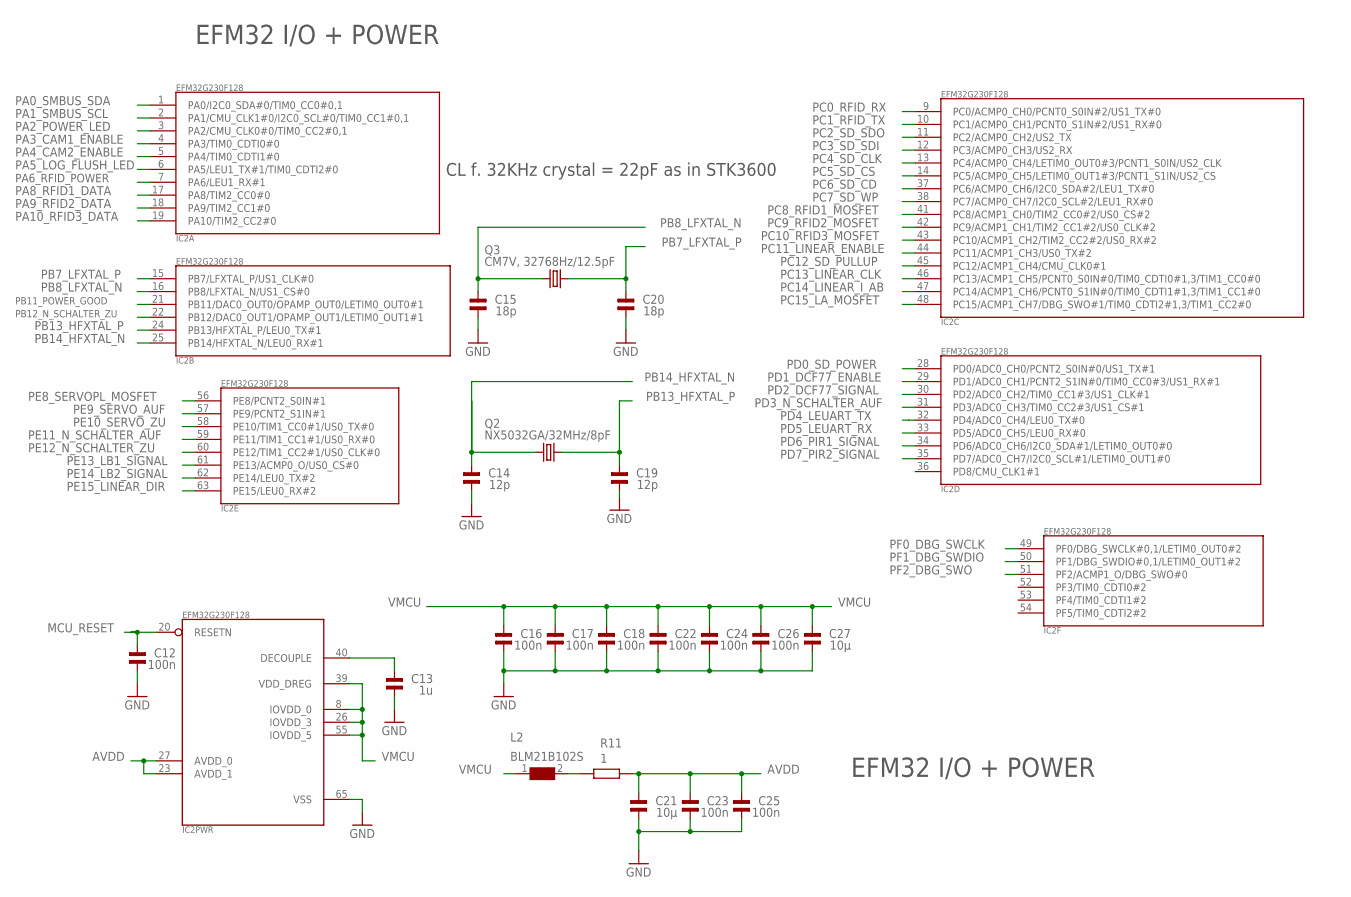
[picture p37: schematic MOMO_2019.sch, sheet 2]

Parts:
C12, C16, C17, C18, C22, C23, C24, C25, C26: 100n; 0805
C13: 1u; 0805
C14, C19: 12p; 0805
C15, C20: 18p; 0805
C21, C27: 10µ; 0805
IC2: EFM32G230F128; QFN64
L2: BLM21B102S; 0805
Q2: NX5032GA/32MHz/8pF; CRYSTAL2P5.0X3.2
Q3: CM7V, 32768Hz/12.5pF; CRYSTAL2P3.2X1.5
R11: 1; R0805

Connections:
AVDD: C21.2, C23.2, C25.2, IC2.23 (AVDD_1), IC2.27 (AVDD_0), R11.2
GND: C12.1, C13.1, C14.1, C15.1, C16.1, C17.1, C18.1, C19.1, C20.1, C21.1, C22.1, C23.1, C24.1, C25.1, C26.1, C27.1, IC2.65 (VSS); also elsewhere on the board
MCU_RESET: C12.2, IC2.20 (RESETN); also elsewhere on the board
unnamed: L2.2, R11.1
unnamed: C13.2, IC2.40 (DECOUPLE)
PA0_SMBUS_SDA: IC2.1 (PA0/I2C0_SDA#0/TIM0_CC0#0,1); also elsewhere on the board
PA1_SMBUS_SCL: IC2.2 (PA1/CMU_CLK1#0/I2C0_SCL#0/TIM0_CC1#0,1); also elsewhere on the board
PA2_POWER_LED: IC2.3 (PA2/CMU_CLK0#0/TIM0_CC2#0,1); also elsewhere on the board
PA3_CAM1_ENABLE: IC2.4 (PA3/TIM0_CDTI0#0); also elsewhere on the board
PA4_CAM2_ENABLE: IC2.5 (PA4/TIM0_CDTI1#0); also elsewhere on the board
PA5_LOG_FLUSH_LED: IC2.6 (PA5/LEU1_TX#1/TIM0_CDTI2#0); also elsewhere on the board
PA6_RFID_POWER: IC2.7 (PA6/LEU1_RX#1); also elsewhere on the board
PA8_RFID1_DATA: IC2.17 (PA8/TIM2_CC0#0); also elsewhere on the board
PA9_RFID2_DATA: IC2.18 (PA9/TIM2_CC1#0); also elsewhere on the board
PA10_RFID3_DATA: IC2.19 (PA10/TIM2_CC2#0); also elsewhere on the board
PB7_LFXTAL_P: C20.2, IC2.15 (PB7/LFXTAL_P/US1_CLK#0), Q3.2
PB8_LFXTAL_N: C15.2, IC2.16 (PB8/LFXTAL_N/US1_CS#0), Q3.1
PB11_POWER_GOOD: IC2.21 (PB11/DAC0_OUT0/OPAMP_OUT0/LETIM0_OUT0#1); also elsewhere on the board
PB12_N_SCHALTER_ZU: IC2.22 (PB12/DAC0_OUT1/OPAMP_OUT1/LETIM0_OUT1#1); also elsewhere on the board
PB13_HFXTAL_P: C19.2, IC2.24 (PB13/HFXTAL_P/LEU0_TX#1), Q2.2
PB14_HFXTAL_N: C14.2, IC2.25 (PB14/HFXTAL_N/LEU0_RX#1), Q2.1
PC0_RFID_RX: IC2.9 (PC0/ACMP0_CH0/PCNT0_S0IN#2/US1_TX#0); also elsewhere on the board
PC1_RFID_TX: IC2.10 (PC1/ACMP0_CH1/PCNT0_S1IN#2/US1_RX#0); also elsewhere on the board
PC2_SD_SDO: IC2.11 (PC2/ACMP0_CH2/US2_TX); also elsewhere on the board
PC3_SD_SDI: IC2.12 (PC3/ACMP0_CH3/US2_RX); also elsewhere on the board
PC4_SD_CLK: IC2.13 (PC4/ACMP0_CH4/LETIM0_OUT0#3/PCNT1_S0IN/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); also elsewhere on the board
PC5_SD_CS: IC2.14 (PC5/ACMP0_CH5/LETIM0_OUT1#3/PCNT1_S1IN/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); also elsewhere on the board
PC6_SD_CD: IC2.37 (PC6/ACMP0_CH6/I2C0_SDA#2/LEU1_TX#0); also elsewhere on the board
PC7_SD_WP: IC2.38 (PC7/ACMP0_CH7/I2C0_SCL#2/LEU1_RX#0); also elsewhere on the board
PC8_RFID1_MOSFET: IC2.41 (PC8/ACMP1_CH0/TIM2_CC0#2/US0_CS#2); also elsewhere on the board
PC9_RFID2_MOSFET: IC2.42 (PC9/ACMP1_CH1/TIM2_CC1#2/US0_CLK#2); also elsewhere on the board
PC10_RFID3_MOSFET: IC2.43 (PC10/ACMP1_CH2/TIM2_CC2#2/US0_RX#2); also elsewhere on the board
PC11_LINEAR_ENABLE: IC2.44 (PC11/ACMP1_CH3/US0_TX#2); also elsewhere on the board
PC12_SD_PULLUP: IC2.45 (PC12/ACMP1_CH4/CMU_CLK0#1); also elsewhere on the board
PC13_LINEAR_CLK: IC2.46 (PC13/ACMP1_CH5/PCNT0_S0IN#0/TIM0_CDTI0#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); also elsewhere on the board
PC14_LINEAR_I_AB: IC2.47 (PC14/ACMP1_CH6/PCNT0_S1IN#0/TIM0_CDTI1#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); also elsewhere on the board
PC15_LA_MOSFET: IC2.48 (PC15/ACMP1_CH7/DBG_SWO#1/TIM0_CDTI2#1,3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); also elsewhere on the board
PD0_SD_POWER: IC2.28 (PD0/ADC0_CH0/PCNT2_S0IN#0/US1_TX#1); also elsewhere on the board
PD1_DCF77_ENABLE: IC2.29 (PD1/ADC0_CH1/PCNT2_S1IN#0/TIM0_CC0#3/US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); also elsewhere on the board
PD2_DCF77_SIGNAL: IC2.30 (PD2/ADC0_CH2/TIM0_CC1#3/US1_CLK#1); also elsewhere on the board
PD3_N_SCHALTER_AUF: IC2.31 (PD3/ADC0_CH3/TIM0_CC2#3/US1_CS#1); also elsewhere on the board
PD4_LEUART_TX: IC2.32 (PD4/ADC0_CH4/LEU0_TX#0); also elsewhere on the board
PD5_LEUART_RX: IC2.33 (PD5/ADC0_CH5/LEU0_RX#0); also elsewhere on the board
PD6_PIR1_SIGNAL: IC2.34 (PD6/ADC0_CH6/I2C0_SDA#1/LETIM0_OUT0#0); also elsewhere on the board
PD7_PIR2_SIGNAL: IC2.35 (PD7/ADC0_CH7/I2C0_SCL#1/LETIM0_OUT1#0); also elsewhere on the board
PE8_SERVOPL_MOSFET: IC2.56 (PE8/PCNT2_S0IN#1); also elsewhere on the board
PE9_SERVO_AUF: IC2.57 (PE9/PCNT2_S1IN#1); also elsewhere on the board
PE10_SERVO_ZU: IC2.58 (PE10/TIM1_CC0#1/US0_TX#0); also elsewhere on the board
PE11_N_SCHALTER_AUF: IC2.59 (PE11/TIM1_CC1#1/US0_RX#0); also elsewhere on the board
PE12_N_SCHALTER_ZU: IC2.60 (PE12/TIM1_CC2#1/US0_CLK#0); also elsewhere on the board
PE13_LB1_SIGNAL: IC2.61 (PE13/ACMP0_O/US0_CS#0); also elsewhere on the board
PE14_LB2_SIGNAL: IC2.62 (PE14/LEU0_TX#2); also elsewhere on the board
PE15_LINEAR_DIR: IC2.63 (PE15/LEU0_RX#2); also elsewhere on the board
PF0_DBG_SWCLK: IC2.49 (PF0/DBG_SWCLK#0,1/LETIM0_OUT0#2); also elsewhere on the board
PF1_DBG_SWDIO: IC2.50 (PF1/DBG_SWDIO#0,1/LETIM0_OUT1#2); also elsewhere on the board
PF2_DBG_SWO: IC2.51 (PF2/ACMP1_O/DBG_SWO#0); also elsewhere on the board
VMCU: C16.2, C17.2, C18.2, C22.2, C24.2, C26.2, C27.2, IC2.8 (IOVDD_0), IC2.26 (IOVDD_3), IC2.39 (VDD_DREG), IC2.55 (IOVDD_5), L2.1; also elsewhere on the board

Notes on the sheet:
EFM32 I/O + POWER
CL f. 32KHz crystal = 22pF as in STK3600

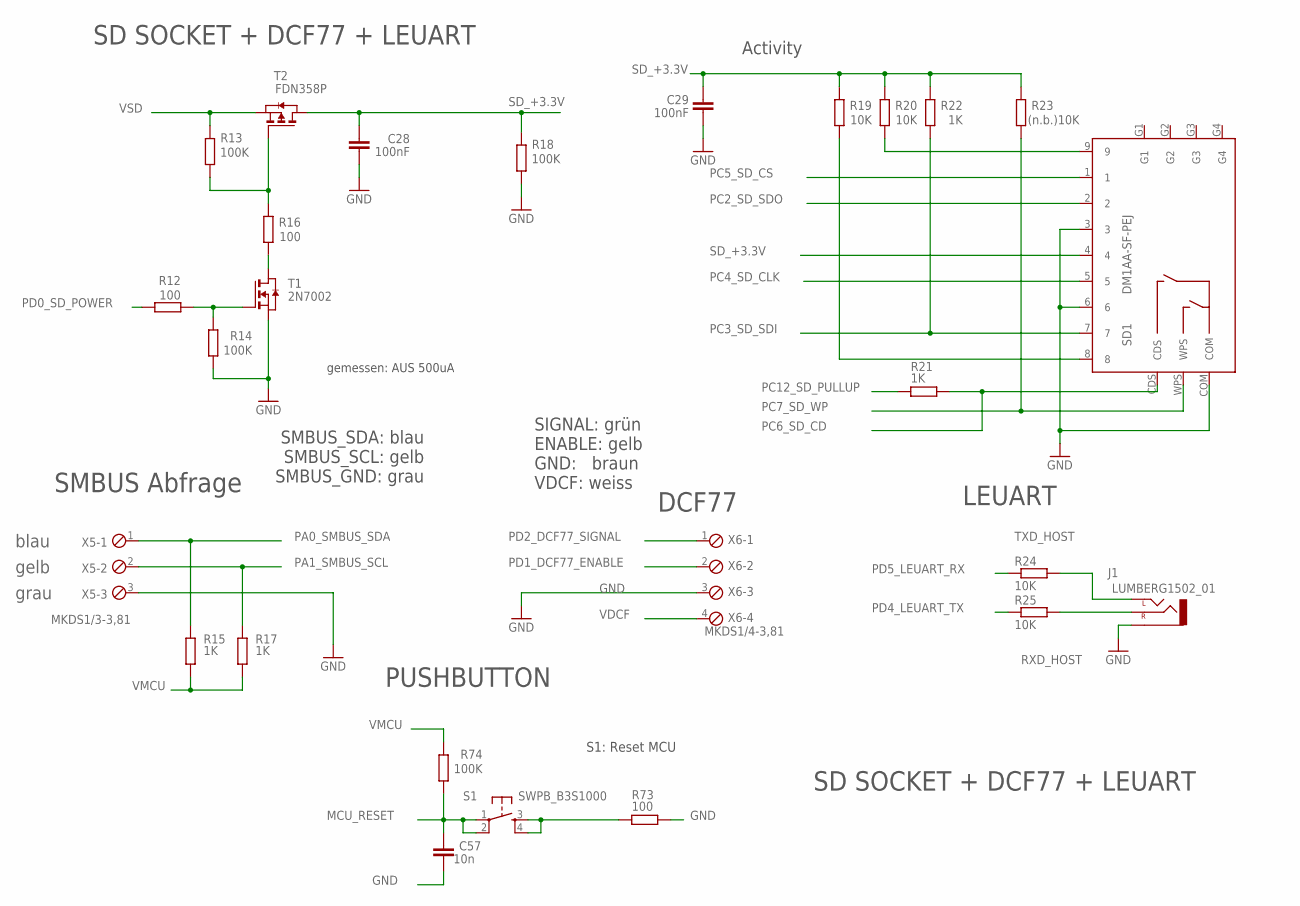
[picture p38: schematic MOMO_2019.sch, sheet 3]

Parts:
C28, C29: 100nF; C0603
C57: 10n; C0603
J1: LUMBERG1502_01
R12, R16, R73: 100; R0805
R13, R14, R18, R74: 100K; R0805
R15, R17, R21, R22: 1K; R0805
R19, R20, R24, R25: 10K; R0805
R23: (n.b.)10K; R0805
S1: SWPB_B3S1000; DTSM-6
SD1: DM1AA-SF-PEJ
T1: 2N7002; ZETEX_SOT-23
T2: FDN358P; ZETEX_SOT-23
X5: MKDS1/3-3,81; 3POL381
X6: MKDS1/4-3,81; 4POL381

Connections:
GND: C28.2, C29.2, C57.1, J1.P$1 (1-SLEEVE), R14.1, R18.1, R73.2, SD1.3, SD1.6, SD1.COM, T1.2 (S), X5.3, X6.3; also elsewhere on the board
MCU_RESET: C57.2, R74.1, S1.1, S1.2; also elsewhere on the board
unnamed: R13.1, R16.2, T2.3 (G)
unnamed: R16.1, T1.1 (D)
unnamed: R12.1, R14.2, T1.3 (G)
unnamed: R20.1, SD1.9
unnamed: R19.1, SD1.8
unnamed: R73.1, S1.3, S1.4
PA0_SMBUS_SDA: R15.1, X5.1; also elsewhere on the board
PA1_SMBUS_SCL: R17.1, X5.2; also elsewhere on the board
PC2_SD_SDO: SD1.2; also elsewhere on the board
PC3_SD_SDI: R22.1, SD1.7; also elsewhere on the board
PC4_SD_CLK: SD1.5; also elsewhere on the board
PC5_SD_CS: SD1.1; also elsewhere on the board
PC6_SD_CD: R21.1, SD1.CDS; also elsewhere on the board
PC7_SD_WP: R23.1, SD1.WPS; also elsewhere on the board
PC12_SD_PULLUP: R21.2; also elsewhere on the board
PD0_SD_POWER: R12.2; also elsewhere on the board
PD1_DCF77_ENABLE: X6.2; also elsewhere on the board
PD2_DCF77_SIGNAL: X6.1; also elsewhere on the board
PD4_LEUART_TX: R25.1; also elsewhere on the board
PD5_LEUART_RX: R24.1; also elsewhere on the board
RXD_HOST: J1.P$3 (3-RIGHT), R25.2
SD_+3.3V: C28.1, C29.1, R18.2, R19.2, R20.2, R22.2, R23.2, SD1.4, T2.1 (D)
TXD_HOST: J1.P$2 (2-LEFT), R24.2
VDCF: X6.4; also elsewhere on the board
VMCU: R15.2, R17.2, R74.2; also elsewhere on the board
VSD: R13.2, T2.2 (S); also elsewhere on the board

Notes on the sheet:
LEUART
gemessen: AUS 500uA
DCF77
Activity
SD SOCKET + DCF77 + LEUART
SIGNAL: grün ENABLE: gelb GND: braun VDCF: weiss
SMBUS Abfrage
blau
gelb
grau
SMBUS_SDA: blau SMBUS_SCL: gelb SMBUS_GND: grau
PUSHBUTTON
S1: Reset MCU

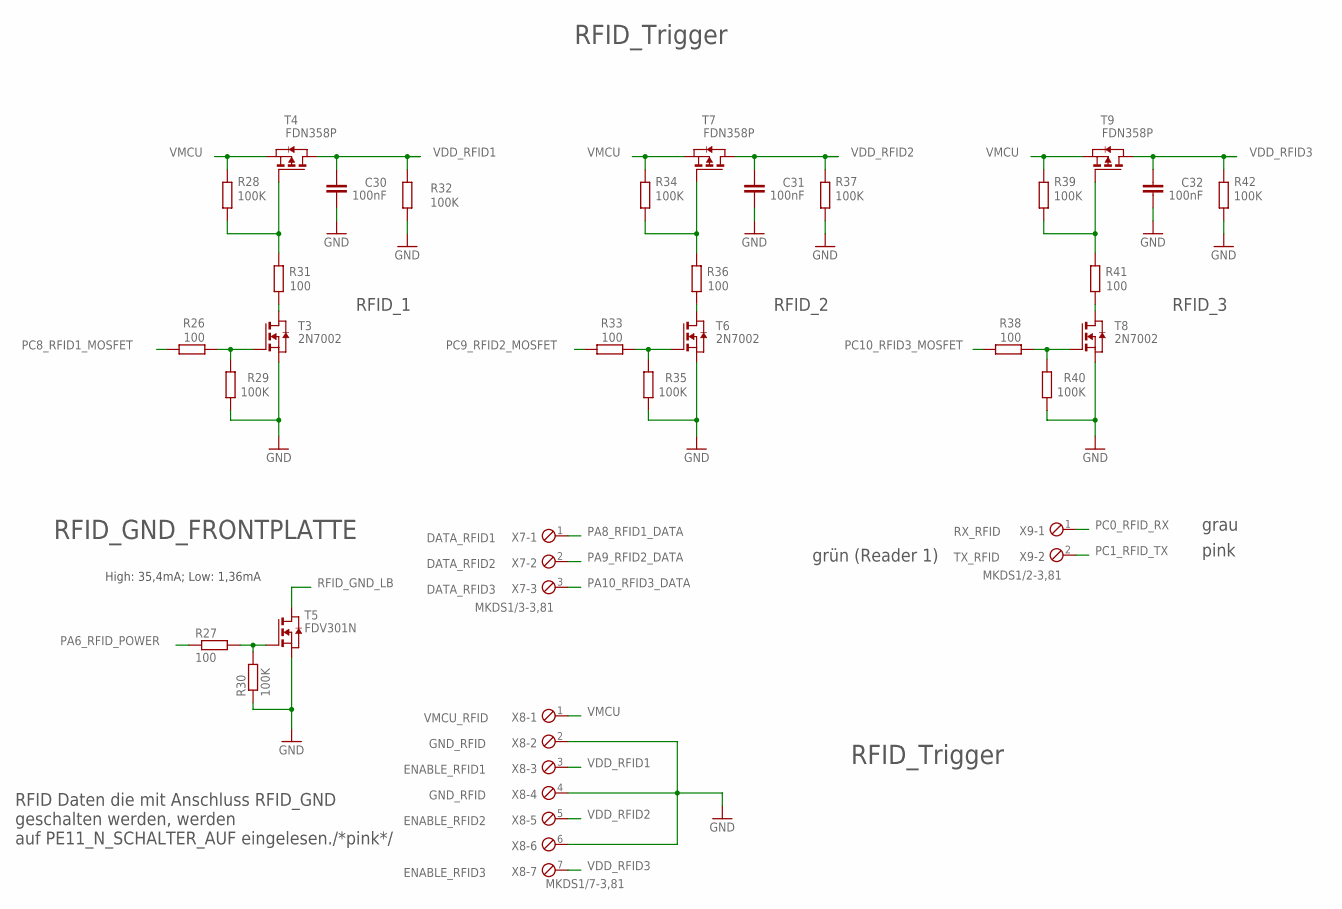
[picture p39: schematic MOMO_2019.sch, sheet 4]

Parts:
C30, C31, C32: 100nF; C0603
R26, R27, R31, R33, R36, R38, R41: 100; R0805
R28, R29, R30, R32, R34, R35, R37, R39, R40, R42: 100K; R0805
T3, T6, T8: 2N7002; ZETEX_SOT-23
T4, T7, T9: FDN358P; ZETEX_SOT-23
T5: FDV301N; SOT-23
X7: MKDS1/3-3,81; 3POL381
X8: MKDS1/7-3,81; 7POL381
X9: MKDS1/2-3,81; 2POL381

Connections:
GND: C30.2, C31.2, C32.2, R29.1, R30.1, R32.1, R35.1, R37.1, R40.1, R42.1, T3.2 (S), T5.2 (S), T6.2 (S), T8.2 (S), X8.2, X8.4, X8.6; also elsewhere on the board
unnamed: R28.1, R31.2, T4.3 (G)
unnamed: R31.1, T3.1 (D)
unnamed: R26.1, R29.2, T3.3 (G)
unnamed: R39.1, R41.2, T9.3 (G)
unnamed: R41.1, T8.1 (D)
unnamed: R27.2, R30.2, T5.3 (G)
unnamed: R38.1, R40.2, T8.3 (G)
unnamed: R34.1, R36.2, T7.3 (G)
unnamed: R36.1, T6.1 (D)
unnamed: R33.1, R35.2, T6.3 (G)
PA6_RFID_POWER: R27.1; also elsewhere on the board
PA8_RFID1_DATA: X7.1; also elsewhere on the board
PA9_RFID2_DATA: X7.2; also elsewhere on the board
PA10_RFID3_DATA: X7.3; also elsewhere on the board
PC0_RFID_RX: X9.1; also elsewhere on the board
PC1_RFID_TX: X9.2; also elsewhere on the board
PC8_RFID1_MOSFET: R26.2; also elsewhere on the board
PC9_RFID2_MOSFET: R33.2; also elsewhere on the board
PC10_RFID3_MOSFET: R38.2; also elsewhere on the board
RFID_GND_LB: T5.1 (D); also elsewhere on the board
VDD_RFID1: C30.1, R32.2, T4.1 (D), X8.3
VDD_RFID2: C31.1, R37.2, T7.1 (D), X8.5
VDD_RFID3: C32.1, R42.2, T9.1 (D), X8.7
VMCU: R28.2, R34.2, R39.2, T4.2 (S), T7.2 (S), T9.2 (S), X8.1; also elsewhere on the board

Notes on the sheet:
RFID_Trigger
RFID_1
RFID_3
RFID_2
RFID_Trigger
RX_RFID
TX_RFID
ENABLE_RFID1
ENABLE_RFID2
ENABLE_RFID3
VMCU_RFID
GND_RFID
DATA_RFID1
DATA_RFID2
DATA_RFID3
pink
grau
High: 35,4mA; Low: 1,36mA
RFID_GND_FRONTPLATTE
grün (Reader 1)
RFID Daten die mit Anschluss RFID_GND geschalten werden, werden auf PE11_N_SCHALTER_AUF eingelesen./*pink*/

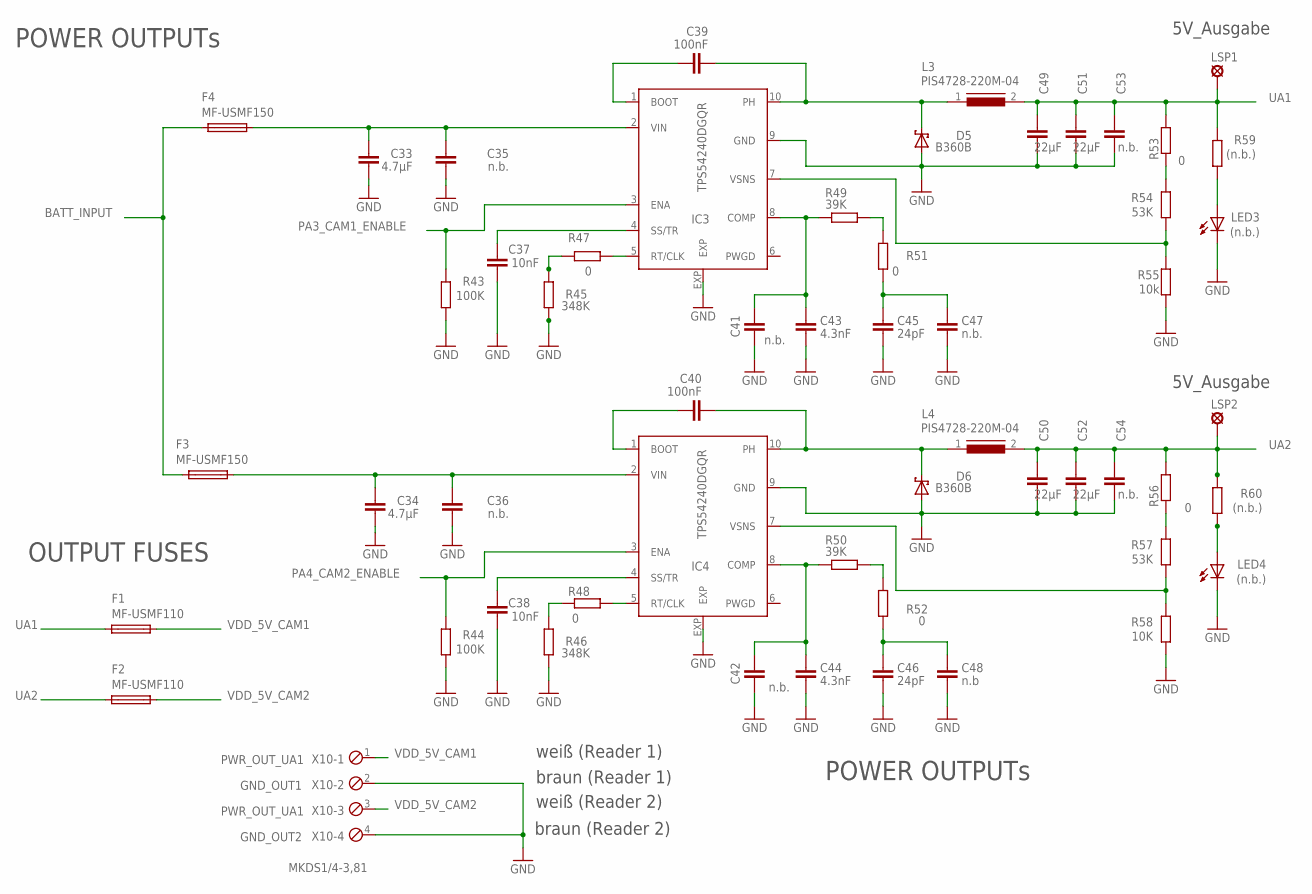
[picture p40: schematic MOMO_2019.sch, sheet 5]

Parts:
C33, C34: 4.7µF; C1210
C35, C36, C53, C54: n.b.; C1210
C37, C38: 10nF; C0603
C39, C40: 100nF; C0603
C41, C42, C47: n.b.; C0603
C43, C44: 4.3nF; C0603
C45, C46: 24pF; C0603
C48: n.b; C0603
C49, C50, C51, C52: 22µF; C1210
D5, D6: B360B; SMB
F1, F2: MF-USMF110; PFUF_1210POLY
F3, F4: MF-USMF150; PFUF_1210POLY
IC3, IC4: TPS54240DGQR; S-PDSO-G10
L3, L4: PIS4728-220M-04; DR127
LED3, LED4: (n.b.); CHIPLED_0805
LSP1, LSP2: (n.b.)SE13; SE13
R43, R44: 100K; R0805
R45, R46: 348K; R0805
R47, R48, R51, R52, R53, R56: 0; R0805
R49, R50: 39K; R0805
R54, R57: 53K; R0805
R55: 10k; R0805
R58: 10K; R0805
R59, R60: (n.b.); R0805
X10: MKDS1/4-3,81; 4POL381

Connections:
BATT_INPUT: F3.P$1 (1), F4.P$1 (1); also elsewhere on the board
GND: C33.2, C34.2, C35.2, C36.2, C37.2, C38.2, C41.2, C42.2, C43.2, C44.2, C45.2, C46.2, C47.2, C48.2, C49.2, C50.2, C51.2, C52.2, C53.2, C54.2, D5.A, D6.A, IC3.9 (GND), IC3.EXP, IC4.9 (GND), IC4.EXP, LED3.C, LED4.C, R43.1, R44.1, R45.1, R46.1, R55.1, R58.1, X10.2, X10.4; also elsewhere on the board
unnamed: C39.2, IC3.1 (BOOT)
unnamed: C39.1, D5.C, IC3.10 (PH), L3.1
unnamed: C37.1, IC3.4 (SS/TR)
unnamed: C41.1, C43.1, IC3.8 (COMP), R49.1
unnamed: C45.1, C47.1, R51.1
unnamed: IC3.7 (VSNS), R54.1, R55.2
unnamed: C40.2, IC4.1 (BOOT)
unnamed: C40.1, D6.C, IC4.10 (PH), L4.1
unnamed: C38.1, IC4.4 (SS/TR)
unnamed: C42.1, C44.1, IC4.8 (COMP), R50.1
unnamed: C46.1, C48.1, R52.1
unnamed: IC4.7 (VSNS), R57.1, R58.2
unnamed: LED4.A, R60.1
unnamed: R45.2, R47.1
unnamed: R46.2, R48.1
unnamed: IC3.5 (RT/CLK), R47.2
unnamed: R49.2, R51.2
unnamed: R53.1, R54.2
unnamed: IC4.5 (RT/CLK), R48.2
unnamed: R56.1, R57.2
unnamed: R50.2, R52.2
unnamed: LED3.A, R59.1
unnamed: C33.1, C35.1, F4.P$2 (2), IC3.2 (VIN)
unnamed: C34.1, C36.1, F3.P$2 (2), IC4.2 (VIN)
PA3_CAM1_ENABLE: IC3.3 (ENA), R43.2; also elsewhere on the board
PA4_CAM2_ENABLE: IC4.3 (ENA), R44.2; also elsewhere on the board
UA1: C49.1, C51.1, C53.1, F1.P$1 (1), L3.2, LSP1.MP, R53.2, R59.2
UA2: C50.1, C52.1, C54.1, F2.P$1 (1), L4.2, LSP2.MP, R56.2, R60.2
VDD_5V_CAM1: F1.P$2 (2), X10.1
VDD_5V_CAM2: F2.P$2 (2), X10.3

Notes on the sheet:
5V_Ausgabe
POWER OUTPUTs
OUTPUT FUSES
PWR_OUT_UA1
GND_OUT1
GND_OUT2
weiß (Reader 1)
braun (Reader 1)
weiß (Reader 2)
braun (Reader 2)

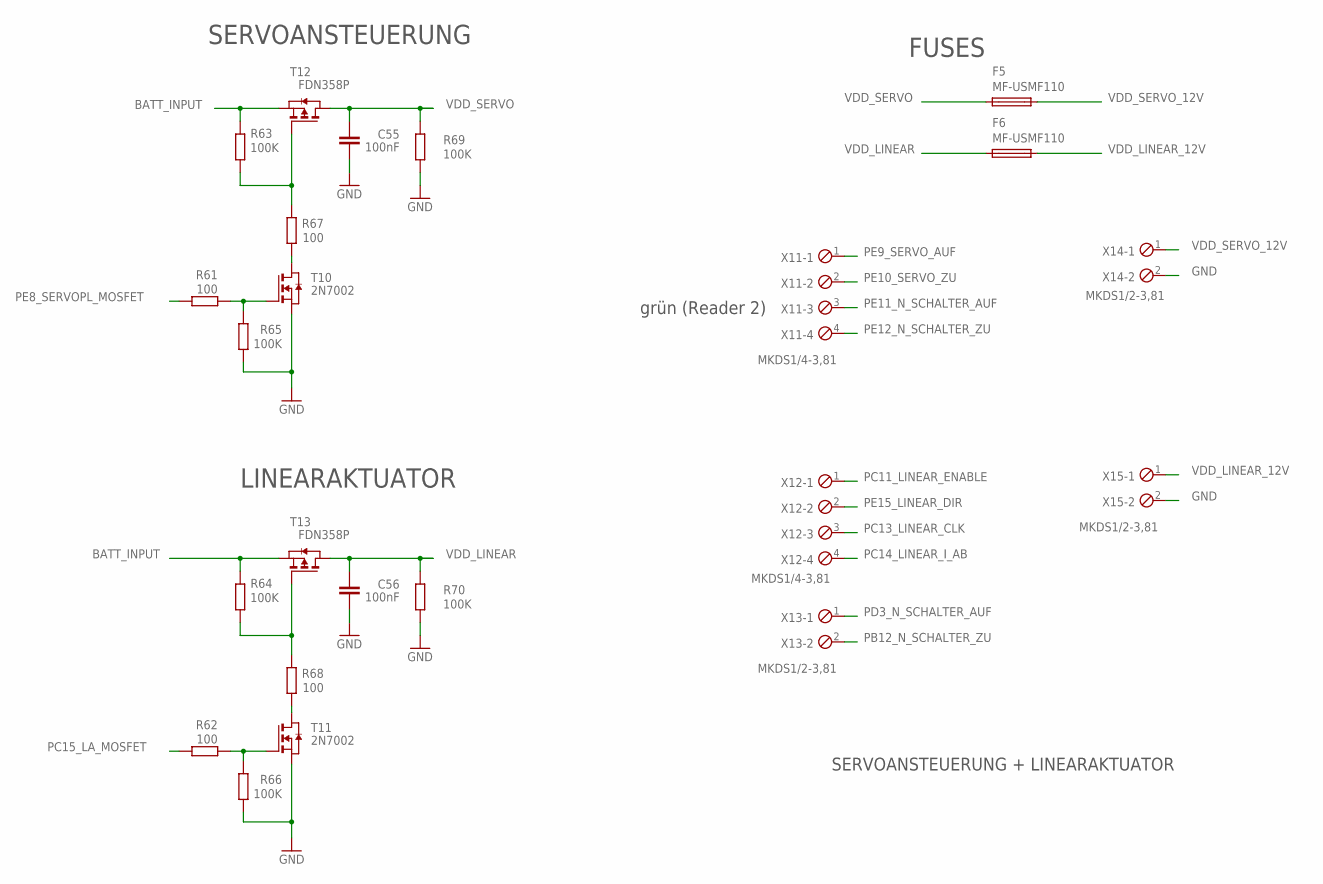
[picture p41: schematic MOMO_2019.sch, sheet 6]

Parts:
C55, C56: 100nF; C0603
F5, F6: MF-USMF110; PFUF_1210POLY
R61, R62, R67, R68: 100; R0805
R63, R64, R65, R66, R69, R70: 100K; R0805
T10, T11: 2N7002; ZETEX_SOT-23
T12, T13: FDN358P; ZETEX_SOT-23
X11, X12: MKDS1/4-3,81; 4POL381
X13, X14, X15: MKDS1/2-3,81; 2POL381

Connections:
BATT_INPUT: R63.2, R64.2, T12.2 (S), T13.2 (S); also elsewhere on the board
GND: C55.2, C56.2, R65.1, R66.1, R69.1, R70.1, T10.2 (S), T11.2 (S), X14.2, X15.2; also elsewhere on the board
unnamed: R63.1, R67.2, T12.3 (G)
unnamed: R67.1, T10.1 (D)
unnamed: R61.1, R65.2, T10.3 (G)
unnamed: R64.1, R68.2, T13.3 (G)
unnamed: R68.1, T11.1 (D)
unnamed: R62.1, R66.2, T11.3 (G)
PB12_N_SCHALTER_ZU: X13.2; also elsewhere on the board
PC11_LINEAR_ENABLE: X12.1; also elsewhere on the board
PC13_LINEAR_CLK: X12.3; also elsewhere on the board
PC14_LINEAR_I_AB: X12.4; also elsewhere on the board
PC15_LA_MOSFET: R62.2; also elsewhere on the board
PD3_N_SCHALTER_AUF: X13.1; also elsewhere on the board
PE8_SERVOPL_MOSFET: R61.2; also elsewhere on the board
PE9_SERVO_AUF: X11.1; also elsewhere on the board
PE10_SERVO_ZU: X11.2; also elsewhere on the board
PE11_N_SCHALTER_AUF: X11.3; also elsewhere on the board
PE12_N_SCHALTER_ZU: X11.4; also elsewhere on the board
PE15_LINEAR_DIR: X12.2; also elsewhere on the board
VDD_LINEAR: C56.1, F6.P$1 (1), R70.2, T13.1 (D)
VDD_LINEAR_12V: F6.P$2 (2), X15.1
VDD_SERVO: C55.1, F5.P$1 (1), R69.2, T12.1 (D)
VDD_SERVO_12V: F5.P$2 (2), X14.1

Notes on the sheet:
SERVOANSTEUERUNG
LINEARAKTUATOR
SERVOANSTEUERUNG + LINEARAKTUATOR
FUSES
grün (Reader 2)

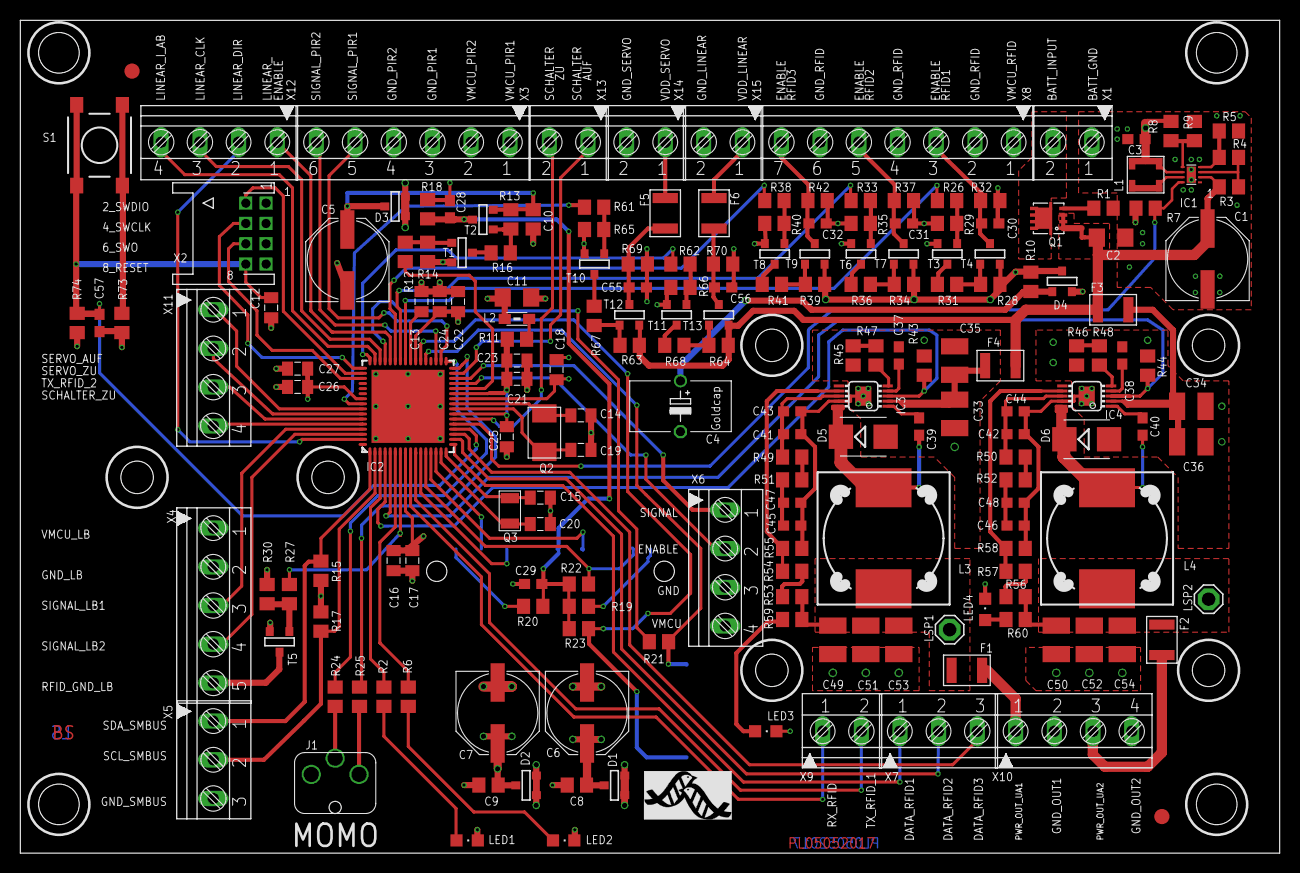
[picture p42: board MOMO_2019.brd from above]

Board: 4 copper layers, 124.0 x 82.0 mm, 192 parts (1 on the bottom side), 132 nets.

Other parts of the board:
U$2: MPIO-ICON

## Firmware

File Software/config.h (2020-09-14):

/***************************************************************************//**
 * @file
 * @brief	Project configuration file
 * @author	Ralf Gerhauser
 * @version	2016-02-27
 *
 * This file allows to set miscellaneous configuration parameters.  It must be
 * included by all modules.
 *
 ****************************************************************************//*
Revision History:
2016-02-26,rage	Increased LOG_BUF_SIZE to 4KB.
2016-02-10,rage	Set DFLT_RFID_POWER_OFF_TIMEOUT to 6 minutes.
2014-11-11,rage	Derived from project "AlarmClock".
*/

#ifndef __INC_config_h
#define __INC_config_h

/*=============================== Header Files ===============================*/

#include <stdio.h>
#include <stdbool.h>
#include "em_device.h"

/*=============================== Definitions ================================*/

/*
 * Basic defines
 */
    /* terminators for lists and strings */

#define	EOL		NULL		/* EndOfList		*/
#define EOS		'\0'		/* EndOfString		*/
#define	NONE		(-1)

    /* macro to calculate the number of elements of an array */
#define ELEM_CNT(array)  (sizeof (array) / sizeof ((array)[0]))

/*
 * LED Definitions for this project
 */
    /*!@brief GPIO Port of the (red) Power-LED. */
#define POWER_LED_PORT		gpioPortA
    /*!@brief GPIO Pin of the (red) Power-LED is PA2. */
#define POWER_LED_PIN		2
    /*! @brief Macro to set or clear the Power-LED */
#define POWER_LED   IO_Bit(GPIO->P[POWER_LED_PORT].DOUT, POWER_LED_PIN)
    /*!@brief GPIO Port of the (green) Log Flush LED. */
#define LOG_FLUSH_LED_PORT	gpioPortA
    /*!@brief GPIO Pin of the (green) Log Flush LED is PA5. */
#define LOG_FLUSH_LED_PIN	5		//! State: 0=OFF, 1=ON
    /*! @brief Macro to set or clear the Log Flush LED */
#define LOG_FLUSH_LED IO_Bit(GPIO->P[LOG_FLUSH_LED_PORT].DOUT, LOG_FLUSH_LED_PIN)

/*!
 * @brief MPU Clock Configuration.
 *
 * Set to 0 to use the internal RC oscillator, if 1 the external 32MHz XTAL
 * is used.  The frequency of the RC oscillator is 14MHz per default.
 */
#define USE_EXT_32MHZ_CLOCK	0

/*
 * Configuration for module "AlarmClock"
 */
    /*!@brief RTC frequency in [Hz]. */
#define RTC_COUNTS_PER_SEC	32768


/*!
 * @brief Interrupt Priority Settings
 *
 * There are 8 priority levels 0 to 7 with 0 to be the highest and 7 to be the
 * lowest priority.  DCF77 (which is called from the EXTI handler) and RTC must
 * use the same priority level to lock-out each other, because they both use
 * function localtime() and this is not multithreading save.  Funktion
 * localtime_r() would be the right choice here, unfortunately it is not
 * available with the IAR compiler library.
 */
#define INT_PRIO_UART	2		//!< UART interrupts for the RFID reader
#define INT_PRIO_LEUART	2		//!< LEUART RX interrupt (not used)
#define INT_PRIO_DMA	2		//!< DMA is used for LEUART
#define INT_PRIO_SMB	2		//!< SMBus used by the battery monitor
#define INT_PRIO_RTC	3		//!< lower priority than others
#define INT_PRIO_EXTI	INT_PRIO_RTC	//!< must be the same as @ref INT_PRIO_RTC


/*
 * Configuration for Atomic Clock module "DCF77.c"
 */
    /*!@brief Use Hardware Enable pin of the DCF77 receiver. */
#define DCF77_HARDWARE_ENABLE	1

    /*!@brief Activate DCF77 only once per day. */
#define DCF77_ONCE_PER_DAY	1

    /*!@brief Call ShowDCF77Indicator() to flash red LED on DCF77 signal. */
#define DCF77_INDICATOR		1


/*
 * Configuration for module "RFID"
 */

    /*!@brief Duration in [s] after which the RFID reader is powered-off. */
#define DFLT_RFID_POWER_OFF_TIMEOUT	360	// 6min

    /*!@brief Duration in [s] during the RFID reader tries to read an ID. */
#define DFLT_RFID_DETECT_TIMEOUT	 20	// 20s


/*
 * Configuration for module "Logging"
 */
    /*!@brief Size of the log buffer in bytes. */
#define LOG_BUF_SIZE	4096

    /*!@brief Use this define to specify a function to be called for monitoring
     * the log activity.  Here, monitoring is done via the LEUART interface.
     */
#define LOG_MONITOR_FUNCTION	drvLEUART_puts

/* forward declaration */
void    drvLEUART_puts(const char *str);

    /*!@brief Disable "alive" message by setting this interval to 0. */
#define LOG_ALIVE_INTERVAL	0


/*!@name DMA Channel Assignment
 *
 * The following definitions assign the 8 DMA channels to the respective
 * devices or drivers.  These defines are used as index within the global
 * @ref DMA_DESCRIPTOR_TypeDef structure @ref g_DMA_ControlBlock.
 */
//@{
#define DMA_CHAN_LEUART_RX	0	//!< LEUART Rx uses DMA channel 0
#define DMA_CHAN_LEUART_TX	1	//!< LEUART Tx uses DMA channel 1
//@}

/*!@brief Name of the configuration file. */
#define CONFIG_FILE_NAME	"CONFIG.TXT"

/*================================== Macros ==================================*/

#ifdef DEBUG
    /*
     * Debugging output via ITM or LEUART
     */
    #if DEBUG_VIA_ITM
	#define DBG_PUTC(ch)	ITM_SendChar(ch)
	#define DBG_PUTS(str)	ITM_SendStr(str)
	uint32_t ITM_SendChar (uint32_t ch);
	void ITM_SendStr(const char *pStr);
    #else
	#define DBG_PUTC(ch)	drvLEUART_putc(ch)
	#define DBG_PUTS(str)	drvLEUART_puts(str)
	void	drvLEUART_putc(char ch);
	void	drvLEUART_puts(const char *str);
    #endif
    void dbgInit(void);
#else
    #define DBG_PUTC(ch)
    #define DBG_PUTS(str)
#endif

#define INCLUDE_DEBUG_TRACE 0
#if INCLUDE_DEBUG_TRACE
    #define DEBUG_TRACE(id)	DebugTrace(id)
    #define DEBUG_TRACE_STOP	DebugTraceStop()
    void DebugTrace(uint32_t id);
    void DebugTraceStop(void);
    #undef  LOG_BUF_SIZE
    #define LOG_BUF_SIZE	2048
    #define DEBUG_TRACE_COUNT	512
#else
    #define DEBUG_TRACE(id)
    #define DEBUG_TRACE_STOP
#endif

    /*! Macro to address a single bit in the I/O range (peripheral range) in
     *  an atomic manner.
     * @param address   I/O register address.
     * @param bitNum    Bit number within this register.
     */
#define IO_BIT_ADDR(address, bitNum)					\
	((__IO uint32_t *) (BITBAND_PER_BASE				\
			+ (((uint32_t)(address)) - PER_MEM_BASE) * 32	\
			+ (bitNum) * 4))

    /*! Shortcut to directly access an I/O-bit. */
#define IO_Bit(regName, bitNum)	*IO_BIT_ADDR(&regName, bitNum)

    /*! Macro to address a single bit in an SRAM variable in an atomic manner.
     * @param address   Address of the variable in SRAM.
     * @param bitNum    Bit number within this variable.
     */
#define SRAM_BIT_ADDR(address, bitNum)					\
	((__IO uint32_t *) (BITBAND_RAM_BASE				\
			+ (((uint32_t)(address)) - RAM_MEM_BASE) * 32	\
			+ (bitNum) * 4))

    /*! Shortcut to directly access a bit in a variable. */
#define Bit(varName, bitNum)	*SRAM_BIT_ADDR(&varName, bitNum)

/*=========================== Typedefs and Structs ===========================*/

/*!@brief Structure to hold Project Information */
typedef struct
{
    char const  ID[12];
    char const  Date[16];
    char const  Time[10];
    char const  Version[16];
} PRJ_INFO;


/*!@brief Enumeration of Alarm Identifiers
 *
 * This is the list of Alarm IDs used by this application.  They are used to
 * identify a particular alarm time entry via the <b>alarmNum</b> parameter
 * when calling alarm functions, e.g. AlarmSet().
 */
typedef enum
{
    ALARM_DCF77_WAKE_UP,    //!< Wake up DCF77 to synchronize the system clock
    ALARM_BATTERY_MON_1,    //!< Time #1 for logging battery status
    ALARM_BATTERY_MON_2,    //!< Time #2 for logging battery status
    ALARM_ON_TIME,          //!< Time when to switch feeder control ON
    ALARM_OFF_TIME,         //!< Time when to switch feeder control OFF
    NUM_ALARM_IDS
} ALARM_ID;

/*
 * !@brief These defines hold the first and last alarm time ENUM for Power
 * Output control, and the number of alarm ON, resp. OFF times.
 */
//@{
#define FIRST_POWER_ALARM	ALARM_ON_TIME
#define LAST_POWER_ALARM	ALARM_OFF_TIME
#define NUM_POWER_ALARMS	(LAST_POWER_ALARM - ALARM_OFF_TIME + 1)
//@}

/*!@brief Enumeration of the EM1 Modules
 *
 * This is the list of Software Modules that require EM1 to work, i.e. they
 * will not work in EM2 because clocks, etc. would be disabled.  These enums
 * are used to set/clear the appropriate bit in the @ref g_EM1_ModuleMask.
 */
typedef enum
{
    EM1_MOD_RFID,	//!<  0: The RFID Module uses the UART
    END_EM1_MODULES
} EM1_MODULES;

/*======================== External Data and Routines ========================*/

extern volatile bool	 g_flgIRQ;		// Flag: Interrupt occurred
extern volatile uint16_t g_EM1_ModuleMask;	// Modules that require EM1


#endif /* __INC_config_h */

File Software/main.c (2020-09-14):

/***************************************************************************//**
 * @file
 * @brief	MAPRLD
 * @author	Ralf Gerhauser
 * @version	2018-11-13
 *
 * This application consists of the following modules:
 * - main.c - Initialization code and main execution loop.
 * - DMA_ControlBlock.c - Control structures for the DMA channels.
 * - Control.c - Sequence Control module.
 * - CfgData.c - Handling of configuration data.
 * - ExtInt.c - External interrupt handler.
 * - AlarmClock.c - Alarm clock and timers facility.
 * - DCF77.c - DCF77 Atomic Clock Decoder
 * - clock.c - An implementation of the POSIX time() function.
 * - LightBarrier.c - Interrupt logic for the two light barriers,
 *   enables the RFID reader.
 * - RFID.c - RFID reader to receive transponder IDs.
 * - BatteryMon.c - Battery monitor, periodically reads the state of the
 *   battery via the SMBus.
 * - LEUART.c - The Low-Energy UART can be used as monitoring and debugging
 *   connection to a host computer.
 * - microsd.c - Together with the files "diskio.c" and "ff.c", this module
 *   provides an implementation of a FAT file system on the @ref ss8.
 * - Logging.c - Logging facility to send messages to the LEUART and store
 *   them into a file on the SD-Card.
 * - PowerFail.c - Handler to switch off all loads in case of Power Fail.
 *
 * Parts of the code are based on the example code of AN0006 "tickless calender"
 * from Energy Micro AS.
 *
 ***************************************************************************//**
 *
 * Parts are Copyright 2013 Energy Micro AS, http://www.energymicro.com
 *
 *******************************************************************************
 *
 * Permission is granted to anyone to use this software for any purpose,
 * including commercial applications, and to alter it and redistribute it
 * freely, subject to the following restrictions:
 *
 * 1. The origin of this software must not be misrepresented; you must not
 *    claim that you wrote the original software.
 * 2. Altered source versions must be plainly marked as such, and must not be
 *    misrepresented as being the original software.
 * 3. This notice may not be removed or altered from any source distribution.
 * 4. The source and compiled code may only be used on Energy Micro "EFM32"
 *    microcontrollers and "EFR4" radios.
 *
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
 * Energy Micro AS will not be liable for any consequential, incidental, or
 * special damages, or any other relief, or for any claim by any third party,
 * arising from your use of this Software.
 *
 ****************************************************************************//*
Revision History:
2020-05-12,rage	Version 1.4:
                - Call CheckAlarmTimes() after CONFIG.TXT has been read.
2018-11-13,rage Version 1.3:
		- Moved DMA related variables to module "DMA_ControlBlock.c".
		- Report available memory (debug version only).
2017-06-20,rage Version 1.2:
		- Specified RFID reader type in array l_RFID_Cfg[].
2017-05-12,rage	Version 1.1:
		- Support for single and double RFID reader configurations,
		  see DUAL_RFID_CONFIGURATION.
		- Power outputs are assigned to the RFID readers and the camera
		  by structures l_RFID_Cfg[] and l_ControlCfg.
		- Updated documentation.
2017-01-22,rage	Initial version for MAPRDL.
*/

/*!
 * @mainpage
 * @section desc Description
 * MAPRDL is an application to control a bird feeder.
 *
 * <b>It consists of the following components:</b>
 *
 * @subsection ssa00 Memory Map
 * FLASH and SRAM memory ranges:
 * <center><table>
 * <tr><th>Address</th> <th>Description</th></tr>
 * <tr><td>0x00000000</td> <td>Start of FLASH, here resides the Booter (32KB)</td></tr>
 * <tr><td>0x00008000</td> <td>Start of Application Software (up to 88KB)</td></tr>
 * <tr><td>0x0001E000</td> <td>EEPROM Emulation Area (8KB)</td></tr>
 * <tr><td>0x0001FFFF</td> <td>End of 128KB FLASH</td></tr>
 * <tr><td>0x10000000</td> <td>Start of SRAM when accessed as Code</td></tr>
 * <tr><td>0x10003FFF</td> <td>End of 16KB SRAM when accessed as Code</td></tr>
 * <tr><td>0x20000000</td> <td>Start of SRAM when accessed as Data</td></tr>
 * <tr><td>0x20003FFF</td> <td>End of 16KB SRAM when accessed as Data</td></tr>
 * </table></center>
 *
 * @subsection ssa01 Microcontroller
 * The heart of the board is an EFM32G230 microcontroller.  It provides two
 * different clock domains: All low-energy peripheral is clocked via a
 * 32.768kHz external XTAL.  The MCU and other high performance peripheral
 * uses a high-frequency clock.  The board can be configured to use the
 * internal RC-oscillator, or an external 32MHz XTAL for that purpose,
 * see define @ref USE_EXT_32MHZ_CLOCK.
 *
 * @subsection ssa02 DCF77 Atomic Clock
 * When powered on, the DCF77 hardware module is enabled to receive the time
 * information and set the system clock.  During this phase, the Power-On LED
 * (i.e. LED1) shows the current state of the DCF signal.  The further behavior
 * depends on the settings in the <i>config.h</i> file.  If the define @ref
 * DCF77_ONCE_PER_DAY is 1, the receiver (and also the LED) will be switched
 * off after time has been synchronized.  As the name of the define suggests,
 * it will be switched on once per day.  To properly detect a change between
 * winter and summer time, i.e. <i>normal time</i> (MEZ) and <i>daylight saving
 * time</i> (MESZ), this happens at 01:55 for MEZ, and 02:55 for MESZ.<br>
 * If the define is 0, the receiver remains switched on, but the LED will only
 * get active again when the time signal gets out-of-sync.<br>
 *
 * @subsection ssa03 Light Barriers
 * The firmware supports two light barriers, currently one is used to detect
 * a bird near the shutter of the feeder.
 *
 * @subsection ssa04 RFID Reader
 * The RFID reader is used to receive the transponder number of the bird, when
 * picking food.  It is enabled by the light barriers and shut down after @ref
 * RFID_PWR_OFF_TIMEOUT seconds when there is no more activity detected.  The
 * transponder @ref ID is looked up in the configuration file to get specific
 * settings for this bird.  When no transponder ID could be detected within
 * @ref RFID_DETECT_TIMEOUT seconds, the bird is treated as <b>UNKNOWN</b>.
 * If an ID is read that is not listed in the configuration file, the bird is
 * treated as <b>ANY</b>.  UNKNOWN and ANY are special IDs in the configuration
 * file to handle these groups of birds.
 * The default values of the timeout defines above may be overwritten by the
 * variables in <a href="../../CONFIG.TXT"><i>CONFIG.TXT</i></a>.
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

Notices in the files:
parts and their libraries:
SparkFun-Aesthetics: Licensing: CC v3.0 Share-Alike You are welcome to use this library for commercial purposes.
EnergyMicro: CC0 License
